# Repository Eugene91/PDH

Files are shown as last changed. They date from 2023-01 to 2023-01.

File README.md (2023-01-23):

# Simple circuit for Pound-Drever-Hall stabilization
The circuit performs heterodyne detection of subcarrier phase from a photodetector 
by mixing it with local oscillator radio-frequency (RF) mixer. 

The circuit has two SMA inputs J1 and J2 for the phased-locked and signal  local oscillator, respectively. 
The scheme of the circuit is depicted below:

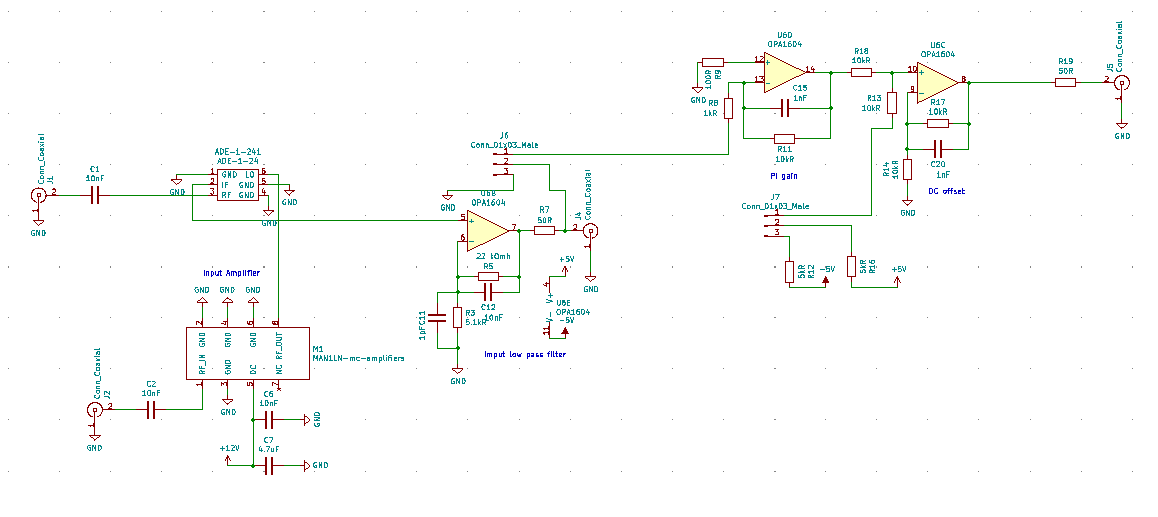
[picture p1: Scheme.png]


- Input signals from J1 and J2 are mixed in RF mixer Minicircuit ADE-1+. 
Prior to coming to mixer the signal from J2 is amplified by Minicircuit MAN1LN.
- The output from the RF mixer is low passed through an active filter based on OPA1604
with 4.5 KHz bandwidth and DC gain of 4.
- The low passed signal is inverted and amplified by inverting amplifier with variable DC gain up to 10 on OPA1604.
- The signal is summed with variable offset and is routed on 50 Ohm load through.

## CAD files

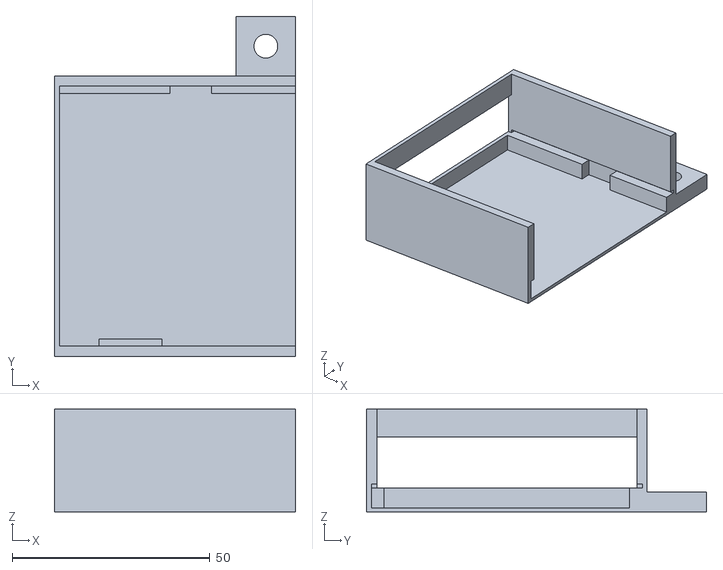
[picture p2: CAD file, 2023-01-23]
Сase for PDH/PDH case.stl
60.9 x 85.9 x 26.0

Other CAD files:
Сase for PDH/PDH case.dwg

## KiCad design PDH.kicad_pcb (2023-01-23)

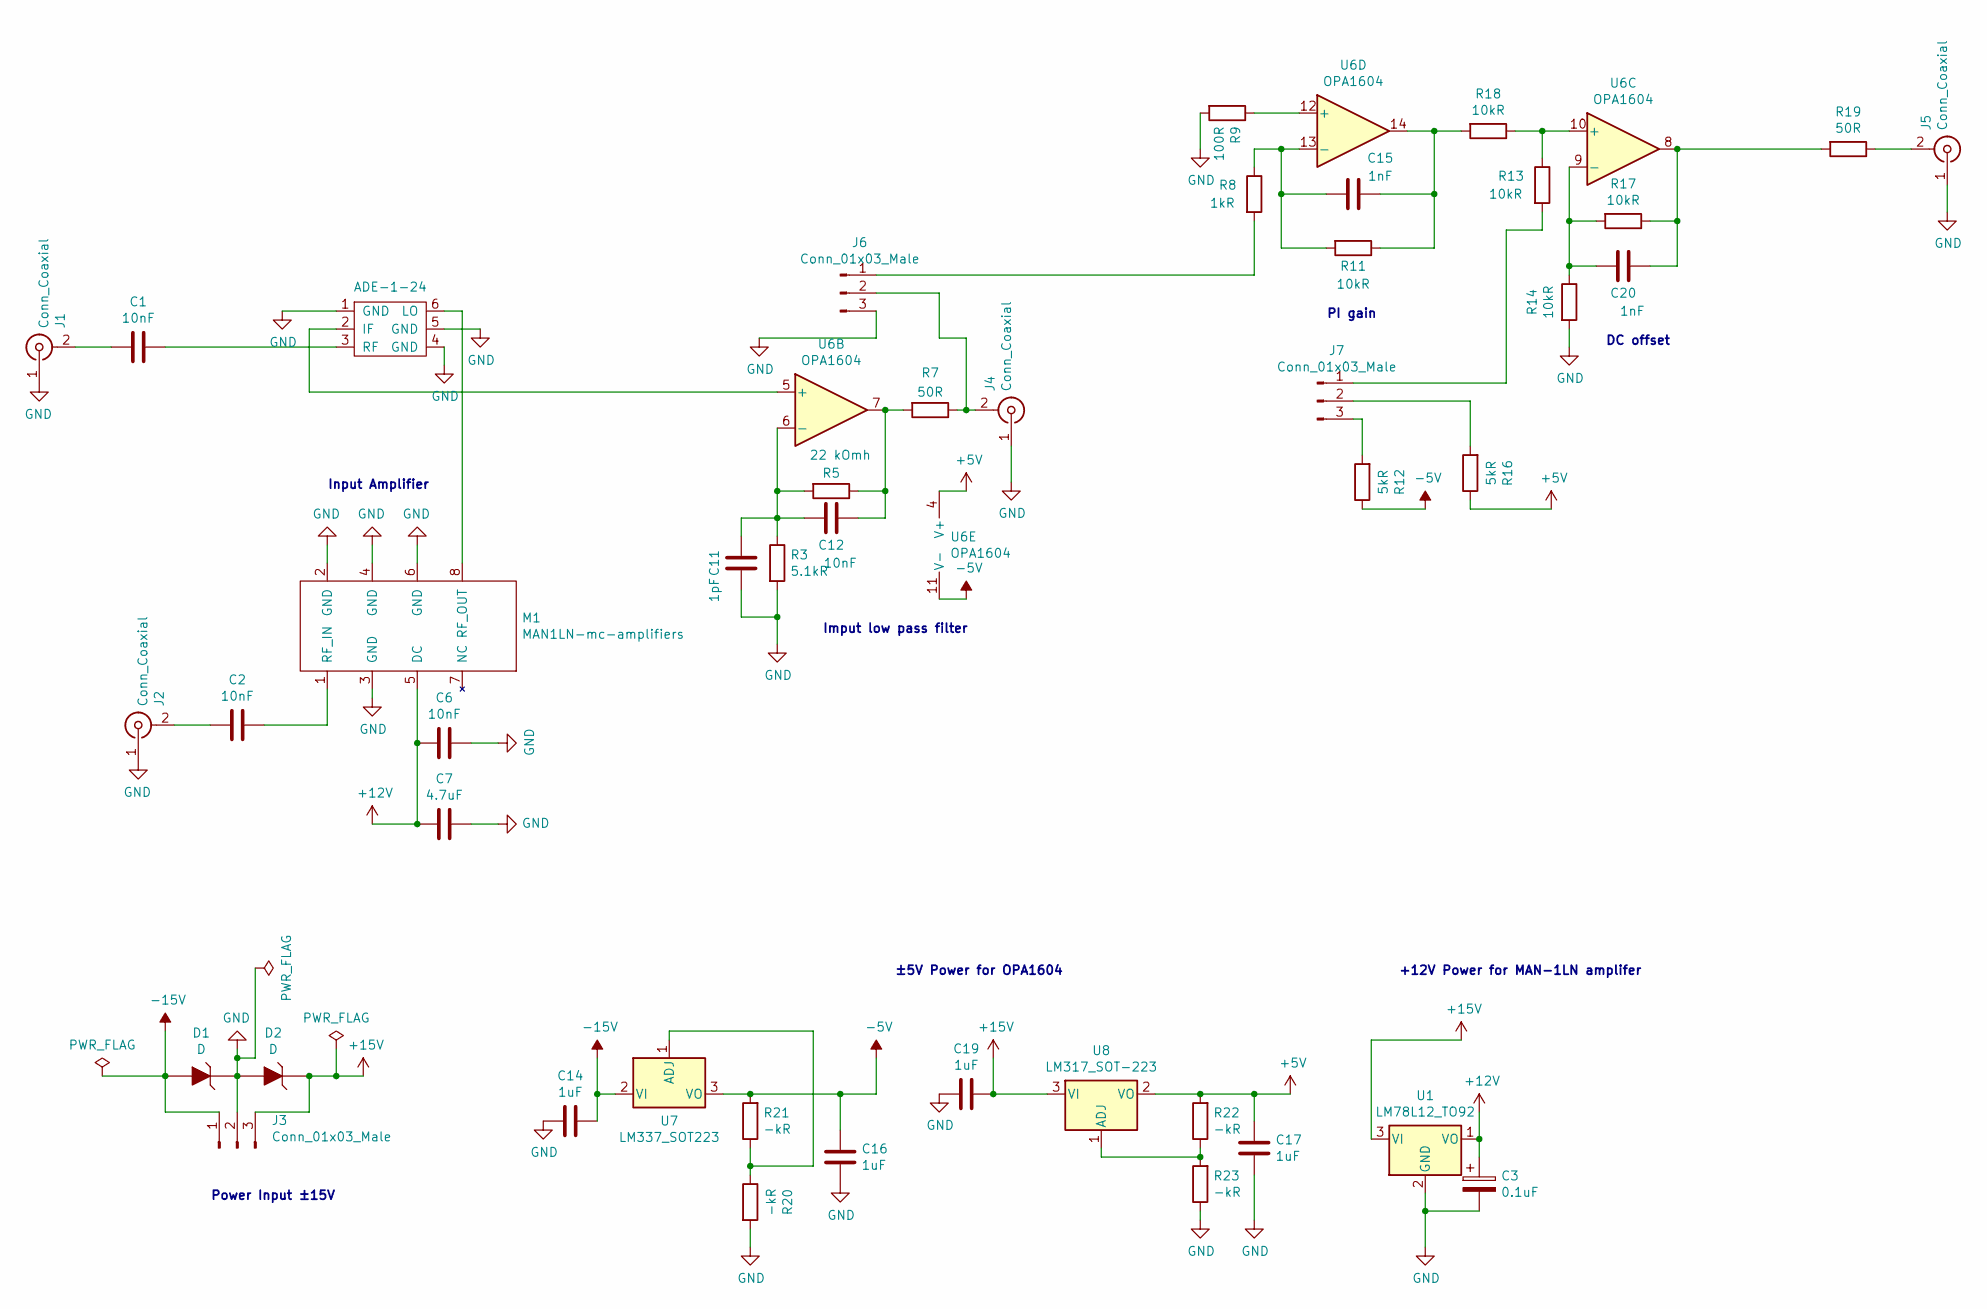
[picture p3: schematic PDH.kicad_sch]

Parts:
C1, C2, C6: 10nF; C_1206
C3: 0.1uF; CP_Radial_D5.0mm_P2.00mm
C7: 4.7uF; C_1206
C11: 1pF; C_0603
C12: 10nF; C_0603
C14, C19: 1uF; 1206
C15: 1nF; C_1206
C16, C17: 1uF; C_0603
C20: 1nF; 0603
D1, D2: D; Photodiode_1206
J1, J2, J4, J5: Conn_Coaxial; RF_SMA_Vertical_5-1814832-1
J3, J6, J7: Conn_01x03_Male; PinHeader_1x3_P2.54_Drill1.1mm
M1: MAN1LN-mc-amplifiers; A05
R3: 5.1kR; R_1206
R5: 22 kOmh; R_1206
R7: 50R; R_Axial_DIN0207_L6.3mm_D2.5mm_P7.62mm_Horizontal
R8: 1kR; R_1206
R9: 100R; R_1206
R11, R14, R17, R18: 10kR; R_1206
R12, R16: 5kR; R_Axial_DIN0207_L6.3mm_D2.5mm_P7.62mm_Horizontal
R13: 10kR; R_Axial_DIN0207_L6.3mm_D2.5mm_P7.62mm_Horizontal
R19: 50R; R_1206
R20, R21, R22, R23: -kR; R_1206
U1: LM78L12_TO92; TO-92-3
U6: OPA1604; TSSOP-14_4.4x5mm_P0.65mm
U7: LM337_SOT223; SOT-223
U8: LM317_SOT-223; SOT-223

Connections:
+5V: C17.1, R16.1, R22.2, U6.4 (V+), U8.2 (VO), U8.4
+12V: C3.1, C6.2, C7.2, M1.5 (DC), U1.1 (VO)
+15V: C19.1, D2.K, J3.3, U1.3 (VI), U8.3 (VI)
-5V: C16.1, R12.1, R21.2, U6.11 (V-), U7.3 (VO)
-15V: C14.1, D1.A, J3.1, U7.2 (VI), U7.4
GND: C3.2, C6.1, C7.1, C11.1, C14.2, C16.2, C17.2, C19.2, D1.K, D2.A, J1.1 (In), J2.1 (In), J3.2, J4.1 (In), J5.1 (In), J6.3, M1.2 (GND), M1.3 (GND), M1.4 (GND), M1.6 (GND), R3.2, R9.2, R14.2, R20.2, R23.1, U1.2 (GND); also elsewhere on the board
unnamed 6: U6.5 (+); also elsewhere on the board
unnamed 7: C1.2; also elsewhere on the board
unnamed 8: M1.8 (RF_OUT); also elsewhere on the board
unnamed: C1.1, J1.2 (Ext)
unnamed: C2.1, J2.2 (Ext)
unnamed: C2.2, M1.1 (RF_IN)
unnamed: C11.2, C12.2, R3.1, R5.2, U6.6 (-)
unnamed: C12.1, R5.1, R7.2, U6.7
unnamed: C15.1, R11.1, R18.2, U6.14
unnamed: C15.2, R8.1, R11.2, U6.13 (-)
unnamed: C20.1, R17.1, R19.2, U6.8
unnamed: C20.2, R14.1, R17.2, U6.9 (-)
unnamed: J4.2 (Ext), J6.2, R7.1
unnamed: J5.2 (Ext), R19.1
unnamed: J6.1, R8.2
unnamed: J7.1, R13.2
unnamed: J7.2, R16.2
unnamed: J7.3, R12.2
unnamed: R9.1, U6.12 (+)
unnamed: R13.1, R18.1, U6.10 (+)
unnamed: R20.1, R21.1, U7.1 (ADJ)
unnamed: R22.1, R23.2, U8.1 (ADJ)

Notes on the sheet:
PI gain
Imput low pass filter
±5V Power for OPA1604
+12V Power for MAN-1LN amplifer
Power Input ±15V
Input Amplifier
DC offset

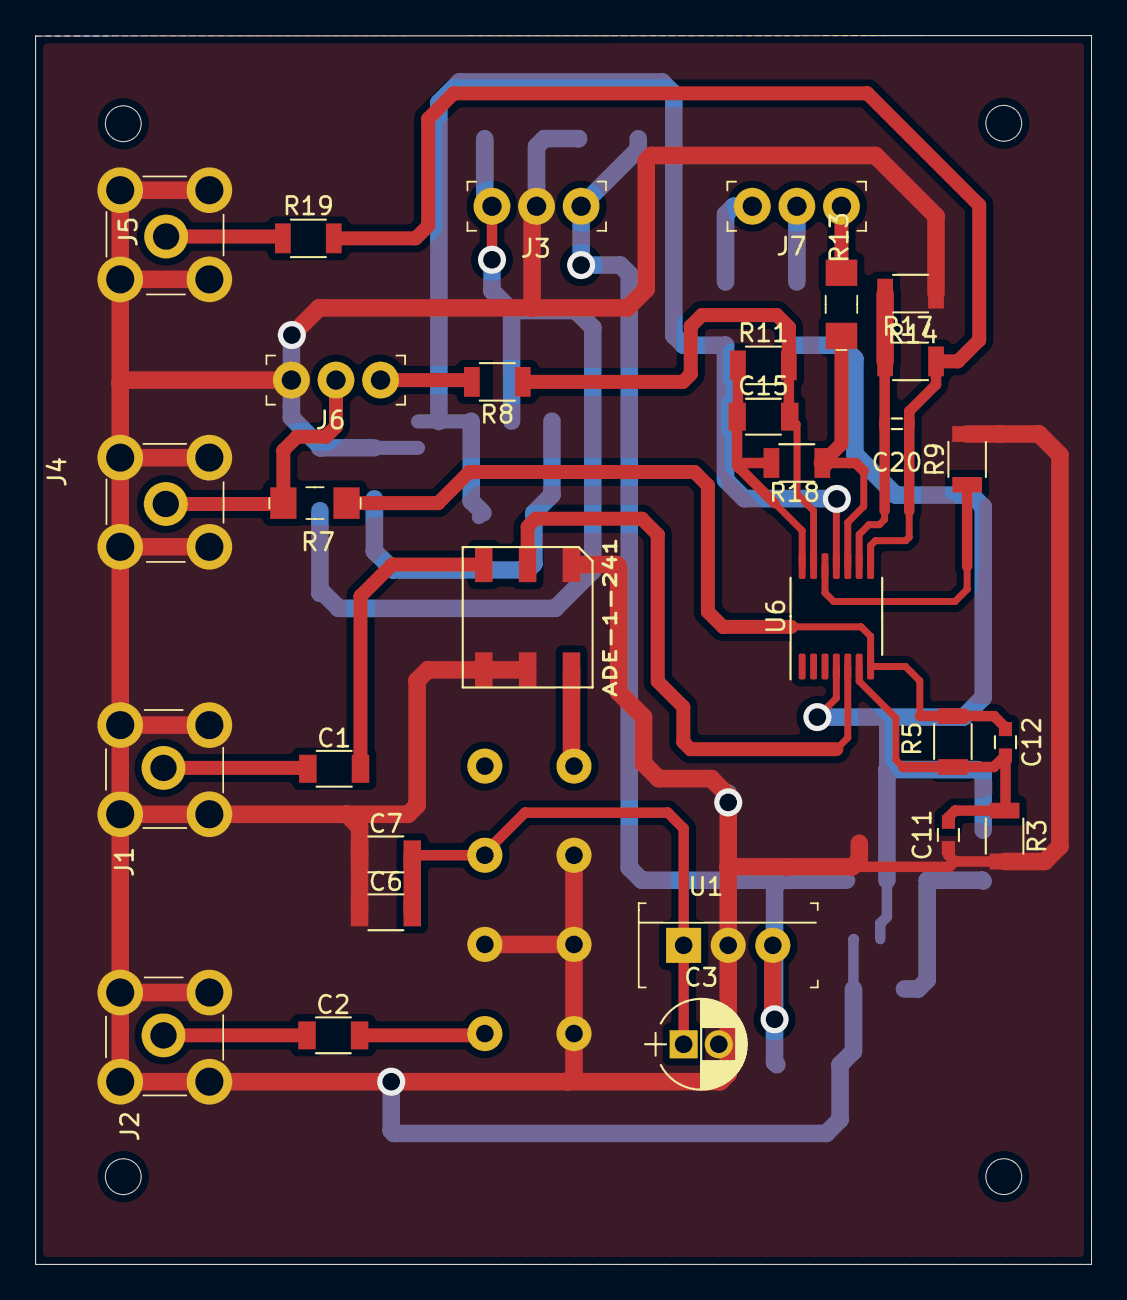
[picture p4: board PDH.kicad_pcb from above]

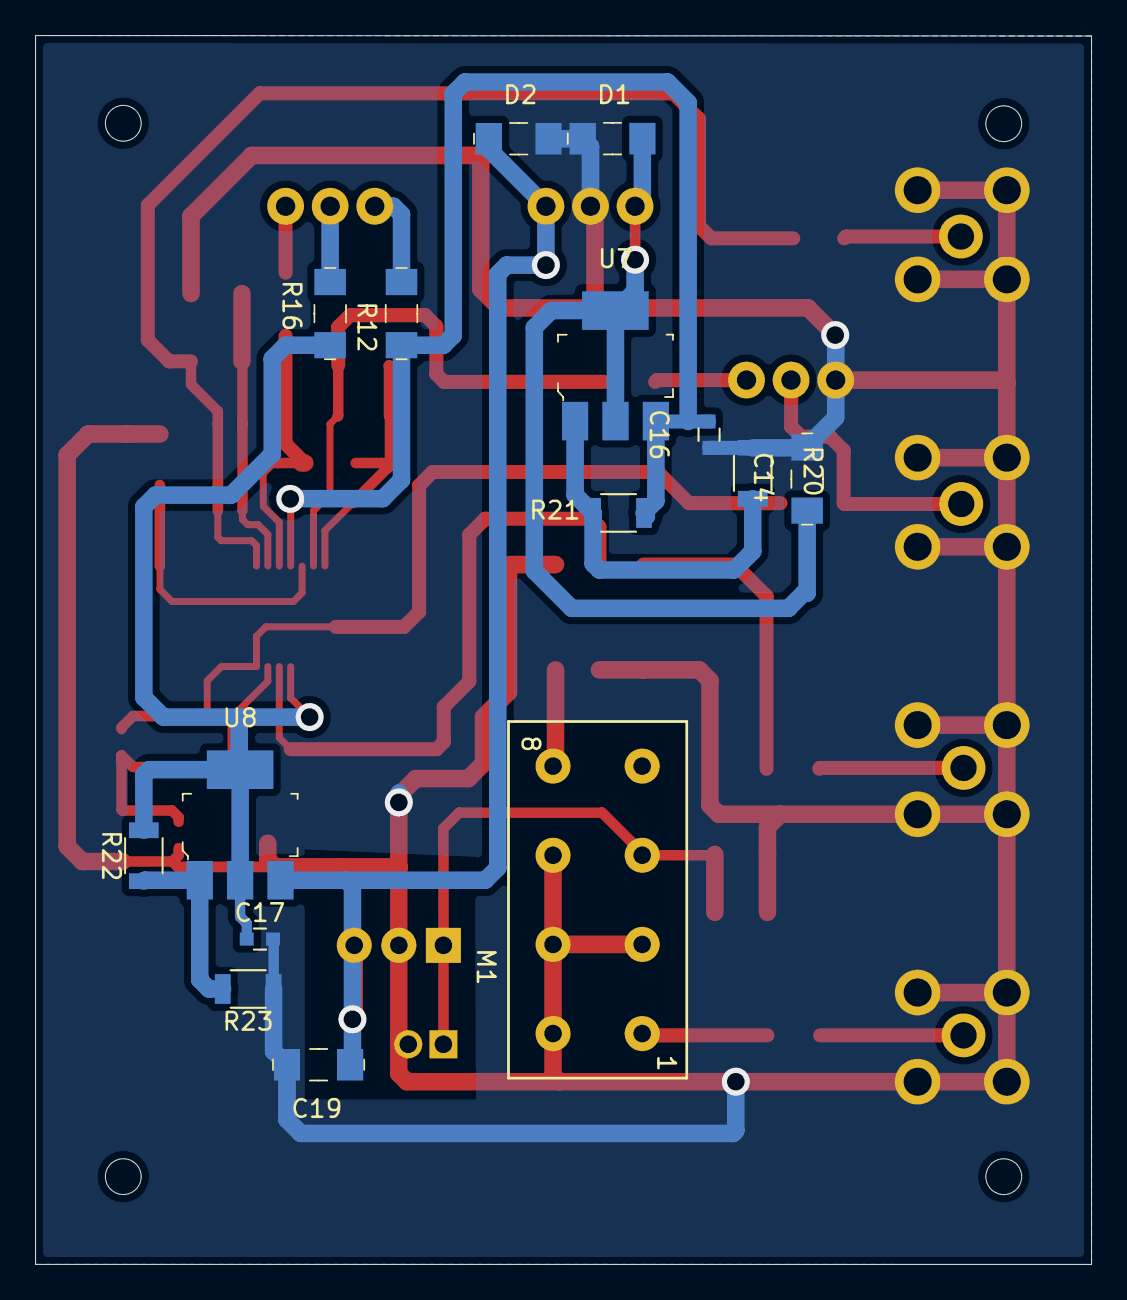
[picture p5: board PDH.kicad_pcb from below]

Board: 2 copper layers, 60.2 x 70.0 mm, 45 parts (15 on the bottom side), 28 nets.

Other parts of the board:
ADE-1-241: ADE-1-24

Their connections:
GND: ADE-1-241.1, ADE-1-241.4, ADE-1-241.5; also elsewhere on the board
unnamed 6: ADE-1-241.2; also elsewhere on the board
unnamed 7: ADE-1-241.3; also elsewhere on the board
unnamed 8: ADE-1-241.6; also elsewhere on the board
